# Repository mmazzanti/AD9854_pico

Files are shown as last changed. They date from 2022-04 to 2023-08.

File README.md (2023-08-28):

# PicoDDS
A Raspberry Pico PCB board that can interface with the AD9854 (and similar others) DDS chips or evaluation boards through parallel port.

# V1.0_beta (future release)
This new version addresses one of the problems in the previous board (see release 0.9), the limit on the LDO current. The new version includes a LT1086 3.3V capable of up to 1.5A. This LDO version however is slightly obsolete, I would suggest to move to a LT1963A for future. At the moment I'm very satisfied with the version 0.9 and even if the LDO is at its limits and getting quite hot the board performs well since production (~ 4 months ago) in our lab.

### Please use always the last firwmare code provided, this is independent on the board version and getting updated/fixed from time to time.
<a href="https://www.buymeacoffee.com/mmazzanti" target="_blank">Buy Me A Coffee</a>

# V0.9
## Why ?
This project was inspired by the necessity of having a simple python/serial interface to easily control older DDS evaluation boards (e.g. the  Eval-AD9854 here described).

The [Eval-AD9854](https://www.analog.com/en/design-center/evaluation-hardware-and-software/evaluation-boards-kits/EVAL-AD9854.html "Eval-AD9854") is an "old" evaluation board for the [AD9854](https://www.analog.com/en/products/ad9854.html "AD9854") Analog Devices DDS IC. The board permits programming of the AD9854 through a serial or parallel interface. 

While the AD9854 is still alive and in production at the time of writing, the word "old" refers to the serial port interface used in the Eval-AD9854 boards. 

Even though the provided software is not compatible with current Microsoft windows version the hardest part of programming the evaluation board comes from finding a parallel printer cable, perhaps from some electronics "museum".

If you are wondering what the parallel printer port on the Eval-AD9854 looks like, here it is:

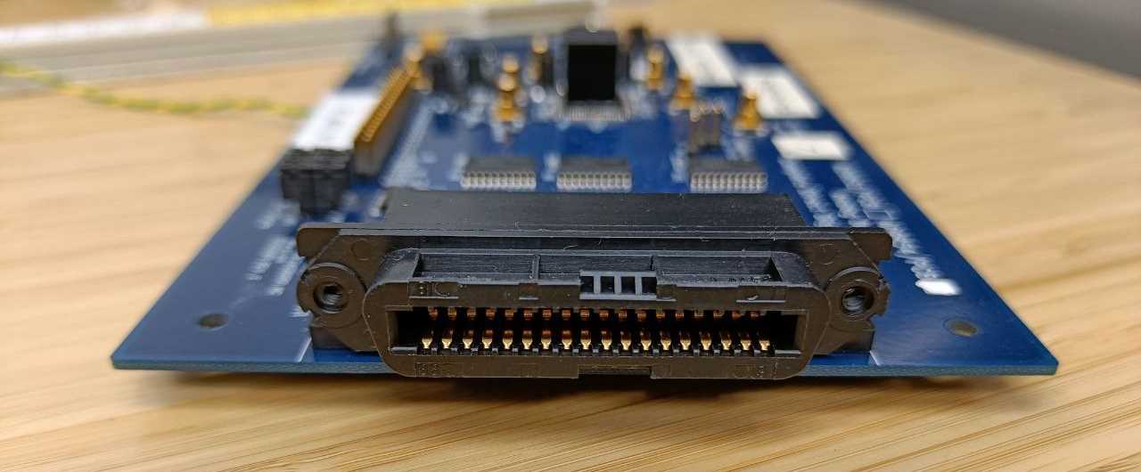
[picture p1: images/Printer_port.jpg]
Parallel_printer Parallel printer connection for millenials and older


Lukily this is not the only interface for programming the evaluation board. A 40 pins IDE port is also available on the board:

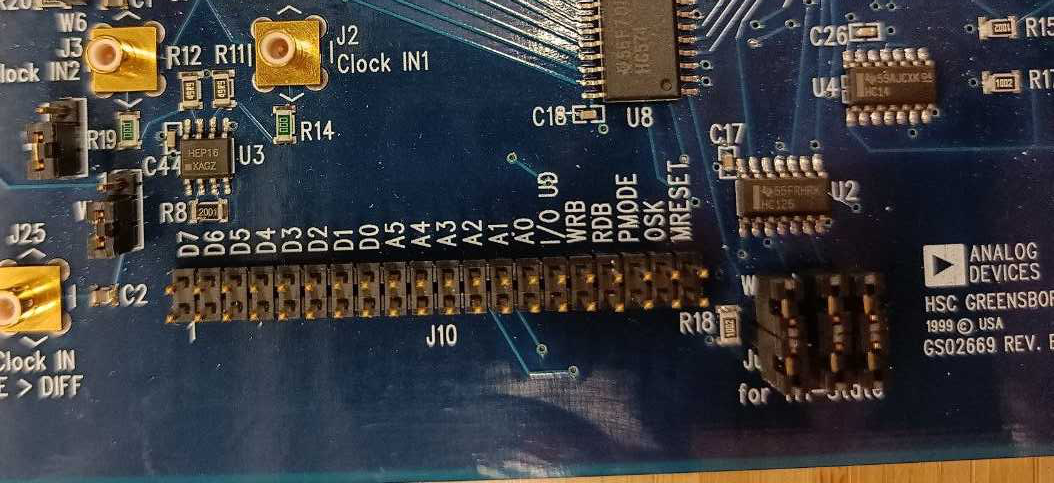
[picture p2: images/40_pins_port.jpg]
40_pins_port The 40 pins IDE port on the Eval-AD99854 board


This looks like a perfect match for any Raspberry Pi board! A custom cable from a Raspberry Pi 3/4 to the Eval-9854 board could be made (as I did for the first prototyping), but this will require a cable per each DDS and a lot of soldering. 
A better idea would be to design a PCB board that interfaces a Raspberry Pi with the DDS evaluation board.
## Why the Pico ? Can I use any Raspberry Pi ?

Sure, any microcontroller capable of handling 21 digital pins can do the job. I decided on  a Raspberry Pico just because of its price tag and small form factor.

## How about powering up the board? 

The evaluation board needs a 3.3V power source to operate. This can also be provided by the same Raspberry. **BEWARE The Eval-9854 can request up to 1A of current at 3.3V, not all Raspberry pi boards can source that amount of power**. When not using the sinc filtering function of the DDS the power consumption goes reduces to ~750mA, when prototyping I used a Raspberry pi 400 and it handled the power hungry DDS quite decently. I would however suggest to power this board externally. The PCB board in this repository takes care also of that. I added a 1A LDO with a screw terminal where one can connect power cables to the Eval-9854; not very elegant, I know,but practical. 

## How to load the "firmware" on the board ? 

Once you are in possession of a PicoDDS board you will have to load on the Raspberry Pico the python source file that you find in the /src folder. The programming of the Pico happens through its micro USB connection. **The USB connection on the board is only for powering the Pico and the Eval-9854; it cannot be used to transfer data to the board!!**

First load a UF2 micropython image on your board (guide [here](https://www.raspberrypi.com/documentation/microcontrollers/micropython.html "micropython")) then load the /src/main.py script on your board. You can do that using [Thonny](https://thonny.org/ "Thonny"), VS code or whatever IDE is now in vogue.

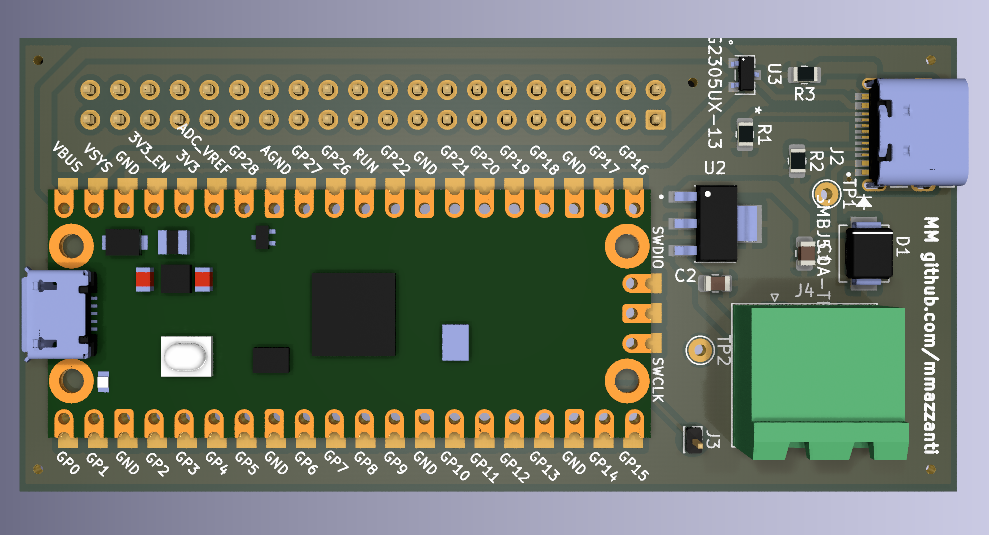
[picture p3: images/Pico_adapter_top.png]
PCB_top|400 PCB board + Raspberry Pico for AD9854


## How to program the AD9854 ? 

The AD9854 permits various modes of operation:
- Single tone mode : in this mode we output a single pre-programmed frequency
- FSK : In this mode it is possible to switch between two pre-programmed frequencies
- Ramped FSK : As the previous but with ramping the frequency up/down when switching
- Chirp : A.k.a. as pulsed FM mode, starting from an initial frequency it ramps up (linearly or not linearly) for the programmed time.
- BPSK : Select between two pre-programmed phase offsets

More precise description can be found on the AD9854 datasheet.

## Why do I need this ?

My tipycal day usage of the AD9854 is to drive some AOM in our laboratory (check out [here](http://hyqs.nl/ "Hyqs") why we want to do that).

An [AOM](https://www.rp-photonics.com/acousto_optic_modulators.html "AOM") (Acousto Optic Modulator) is nothing more than a cyrstal vibrating at a certain frequency capable of steering a laser beam and adding-subtracting its resonating frequency to the diffracting beam (read more here ).

The typical resonating frequencies of AOM are between 70-300MHz although the coverage of this bandwith is mostly wavelength dependent.

In my case I needed a signal at 150MHz and I appeared to have found some Eval-AD9854 boards in some "storage" around (what a lucky find :blush: )

## Clocking the AD9854

One of the parameters hard coded in the main.py file is the clocking speed. The AD9854 can be clocked at 300MHz max. It has an internal PLL clock multiplier in case only slower clocks are available. The board I've been using so far has a 60MHz oscillator on it, however for more phase-dependent applications I plan to use a 10MHz clock reference from an atomic clock in future. The maximum clock multiplier is 20 that would mean that using directly a 10MHz clock and a x20 multiplier will push my clocking speed to 200MHz. In this case one can use a second DDS to generate a higher frequency clock or a second PLL clock multiplier.

Set the following variables depending on your clocking speed :
- SYSCLK : Provided clock speed (frequency of whatever you connect to the clock input port). In my case SYSCLK = 60E6.
- CLKMULT : Clock multiplier value, this will define the maximum frequency that can be generated by the DDS. In my case CLKMULT = 4 --> I'm clocking the DDS at 4*60MHz = 240MHz frequency and the highest output frequency I can get is 120MHz.
- WR_D_A(0x20, 0x60) : This is defined inside the _Init_AD9854()_ function. If you want to enable sinc filtering, replace it to _WR_D_A (0x20, 0x60) **BEWARE : This raises the total power consumption to 1.1A (1A AD9854 + 100mA for the Pico), which is 100mA higher than the on-board LDO's capability**. It should be enabled only when the Pico is connected through its micro-usb connection. In this configuration the mossfet will set the micro-usb as power source for the Pico and avoid over-loading the LDO. I will provide soon a V2 of the board with an updated LDO that can output up to 1.5A.
## How to use the micropython script

Various functions are available from the source script. These don't cover all the capabilities of the AD9854 but only what I need in the lab. More functions might be added in the future if I need them. Feel free to fork this repository if you want to add more!

After connecting to the Pico the following functions are available from the serial terminal.

- SingleTone(freq,ampl) : Turns on the AD9854 at the input frequency. freq must be declared in hertz. This corresponds to the single tone mode of the DDS. The amplitude of the signal can be selected with the "ampl" parameter [0-4095].
- on(freq,ampl) : To be used after initializing the DDS (by calling _SingleTone()_). Sets the output frequency and amplitude in single tone operational mode.
- off() : Turns off the DDS output (sets it to the lowest amplitude).
- UFSK(freq1, freq2, ampl) : Sets the AD9854 in FSK mode, the lowest frequency between freq1 and freq2 will be outputted immediately. To switch between the two frequencies one can use the Switch() function.
- RUFSK(freq1, freq2, ampl, delta, N) : Switches between freq1 and freq2 going through a linear ramp between the two. This corresponds to the ramped-FSK mode of the DDS. N is the number of steps the counter will need before switching to the next frequency. The switching period is given by (N-1)*system_clock. "delta" is the frequency step incremented each time the counter reaches 0
- Switch() : Switches between freq1 and freq2.

## No, I don't want to order your board!

Then no problem, the board just simplifies the connection. If you don't want to order a board or just test if the DDS works for you or any other reasons you can just connect 20 of the 40 pins connection to your Raspberry Pico (or 3/4) and start using generating RF frequencies immediately!
<br/>
<br/>
**BEWARE :** powering the DDS is now up to you. Find a 3.3V 1A power source (better if 1.5A).
<br/>
<br/>
Connect the Pico and the Eval-9854 as following:

- GP16 -> MRESET
- GP15 -> OSK
- GP17 -> PMODE
- GP14 -> RDB
- GP18 -> WRB
- GP13 -> I/O UD
- GP2 -> FSK (this can be found on the pin W9 on the board)
- GP19 -> A0
- GP12 -> A1
- GP20 -> A2
- GP11 -> A3
- GP21 -> A4
- GP10 -> A5
- GP22 -> D0
- GP9 -> D1
- GP8 -> D2
- GP7 -> D3
- GP6 -> D4
- GP5 -> D5
- GP4 -> D6
- GP3 -> D7

Or replace the Pins number in the python source file. A Raspberry pico can be connected using dupont wires as following :

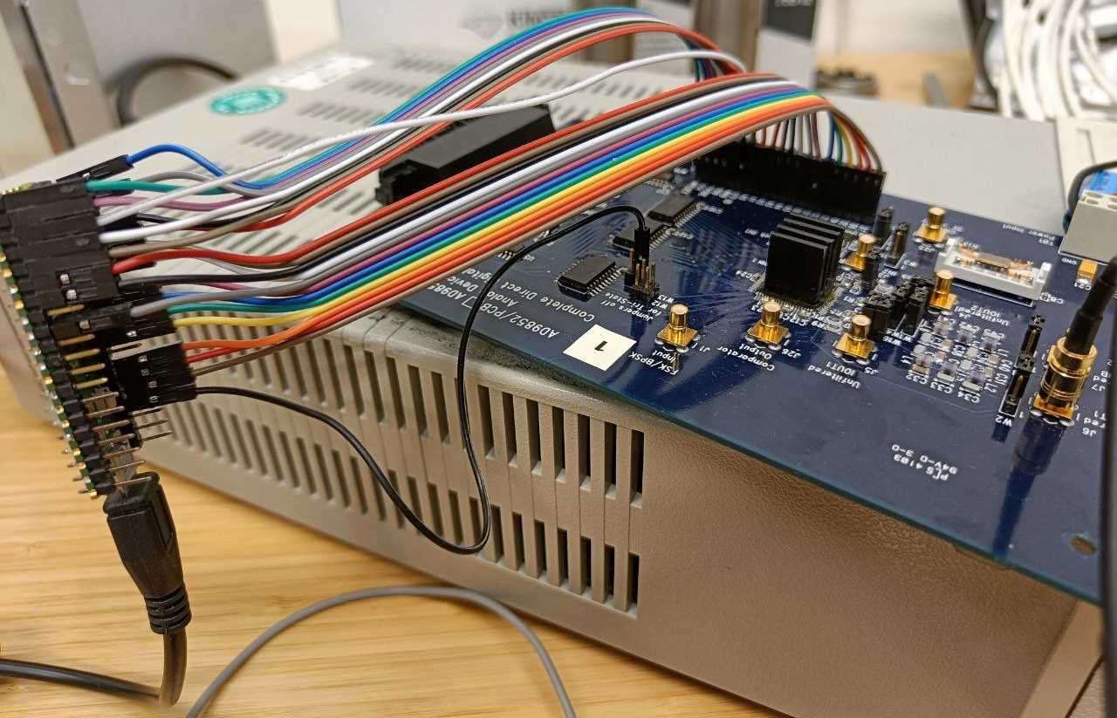
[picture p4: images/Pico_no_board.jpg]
Pico_no_board|400 A Raspberry Pico connected to an Eval-AD9854 using dupont wires


Notice the black wire going on the pin W9, this is used for the FSK bit.

## Performances

### Switching time :

Time required to switch off -> on the RF signal.
It takes ~6ms from the moment one calls the _on(freq,ampl)_ (T=0 in the picture) to the moment when the AD9854 gives an output. 
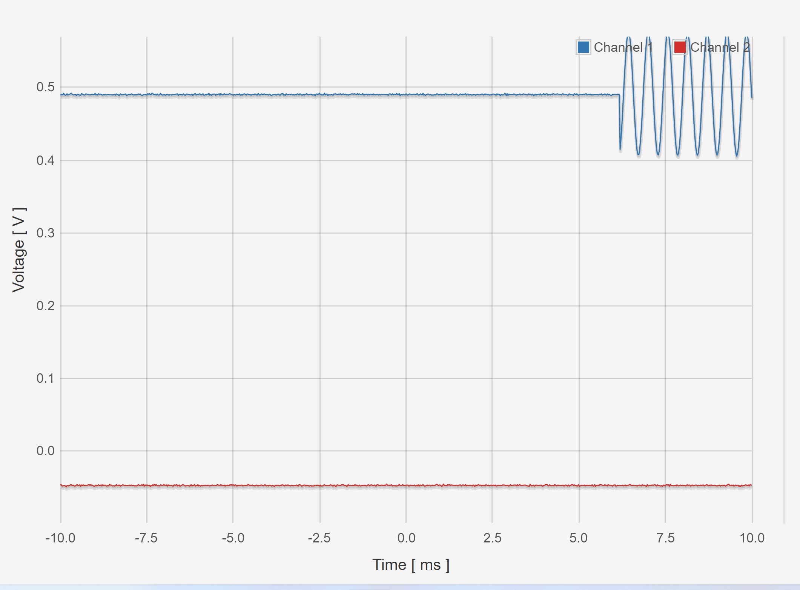
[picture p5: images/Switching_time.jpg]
Switching time On/Off switching time


### Frequency sweep :

This is an example of a frequency sweep :

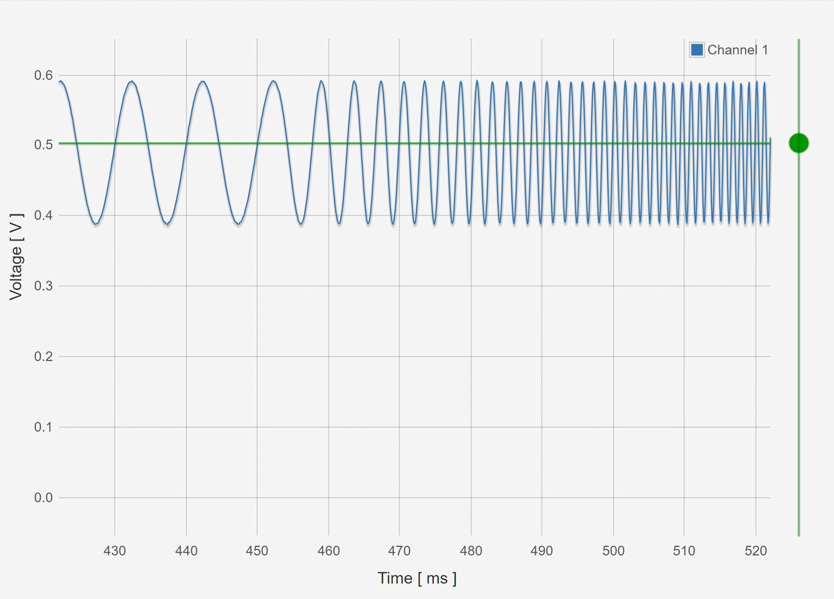
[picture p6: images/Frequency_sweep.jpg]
Frequency sweep


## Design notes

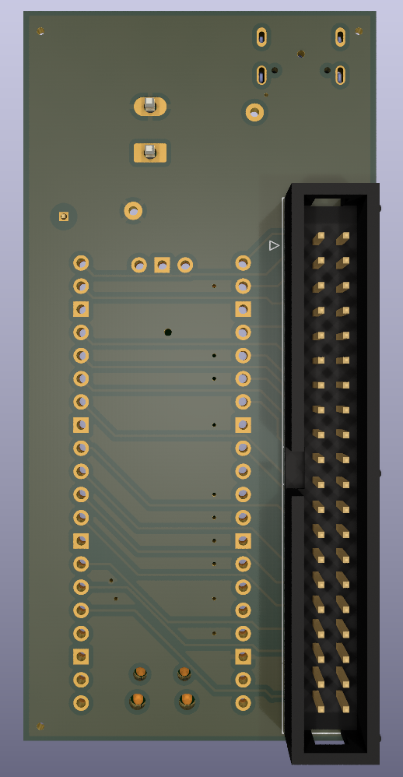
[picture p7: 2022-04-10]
images/Pico_adapter_bottom.png

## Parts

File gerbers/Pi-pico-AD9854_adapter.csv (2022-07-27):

Id | Designator | Package | Quantity | Designation | Supplier and ref
1 | U2 | LT1086 | 1 | LT1086-3.3
2 | TP2,TP1 | TestPoint_THTPad_D2.0mm_Drill1.0mm | 2 | TestPoint
3 | R1,R2 | R_0805_2012Metric | 2 | 5.1k
4 | J4 | PhoenixContact_MSTBA_2,5_2-G-5,08_1x02_P5.08mm_Horizontal | 1 | Screw_Terminal_01x02
5 | D1 | SMBJ5.0A-TR | 1 | SMBJ5.0A-TR
6 | U3 | DMG2305UX-13 | 1 | DMG2305UX-13
7 | U1 | RPi_Pico_SMD_TH | 1 | Pico
8 | R3 | R_0805_2012Metric | 1 | 0
9 | J2 | HRO_TYPE-C-31-M-12 | 1 | TYPE-C-31-M-12
10 | C2,C1 | CP_EIA-2012-12_Kemet-R | 2 | 10uF
11 | J3 | Pin_D1.0mm_L10.0mm | 1 | Conn_01x01_Male
12 | J1 | IDC-Header_2x20_P2.54mm_Vertical | 1 | Conn_02x20_Odd_Even

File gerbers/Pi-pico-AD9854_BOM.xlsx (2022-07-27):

Comment | Designator | Footprint | JLCPCB Part #
0.47 uF | C1 | CAP-SMD_0805 | C13967
33uF | C2 | CAP-SMD_0805 | C432920
SMBJ5.0A-TR | D1 | SMB,DO-214AA | C130397
TYPE-C-31-M-12 | J2 | TYPE-C-31_L8.94_W7.3 | C165948
C81276 | J3 | SIP-1_2.54x2.54 | C81276
Screw_connector_terminal | J4 | SIP-2_7.8x10.0x5.0P | C8404
5.1K | R1 | RES-SMD_0805 | C17617
5.1K | R2 | RES-SMD_0805 | C17617
0 | R3 | RES-SMD_0805 | C728267
LT1086IM-3.3#TRPBF | U2 |  | C662441
DMG2305UX-7 | U3 | SOT-23-3 | C150470

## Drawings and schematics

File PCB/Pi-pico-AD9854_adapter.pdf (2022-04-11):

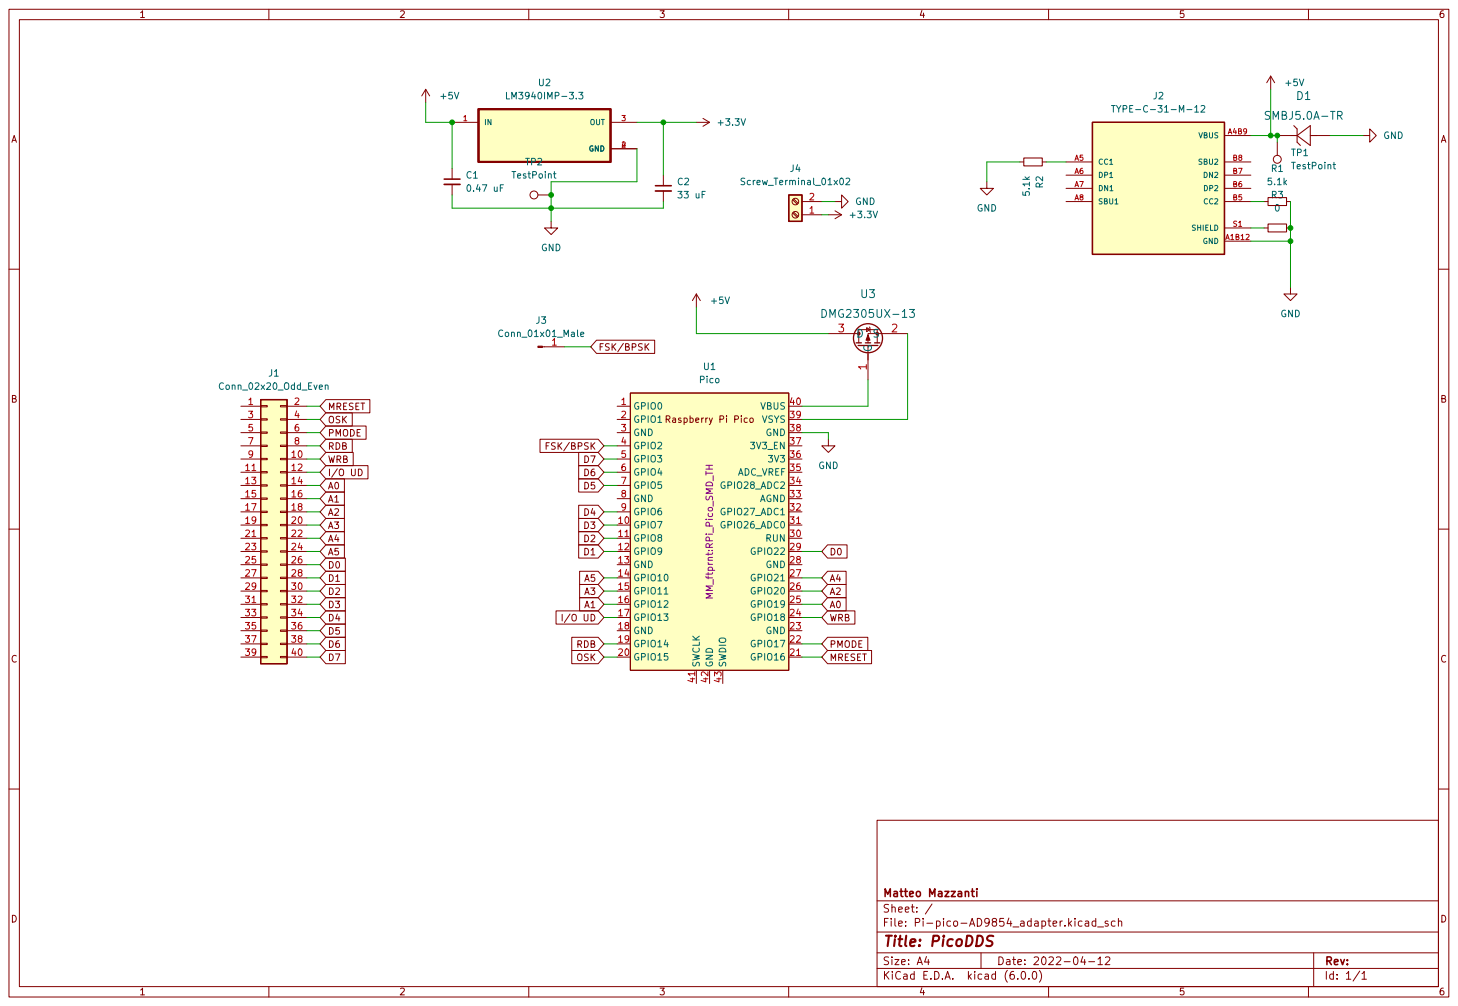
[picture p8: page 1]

File: Pi-pico-AD9854_adapter.kicad_sch Sheet: / Matteo Mazzanti

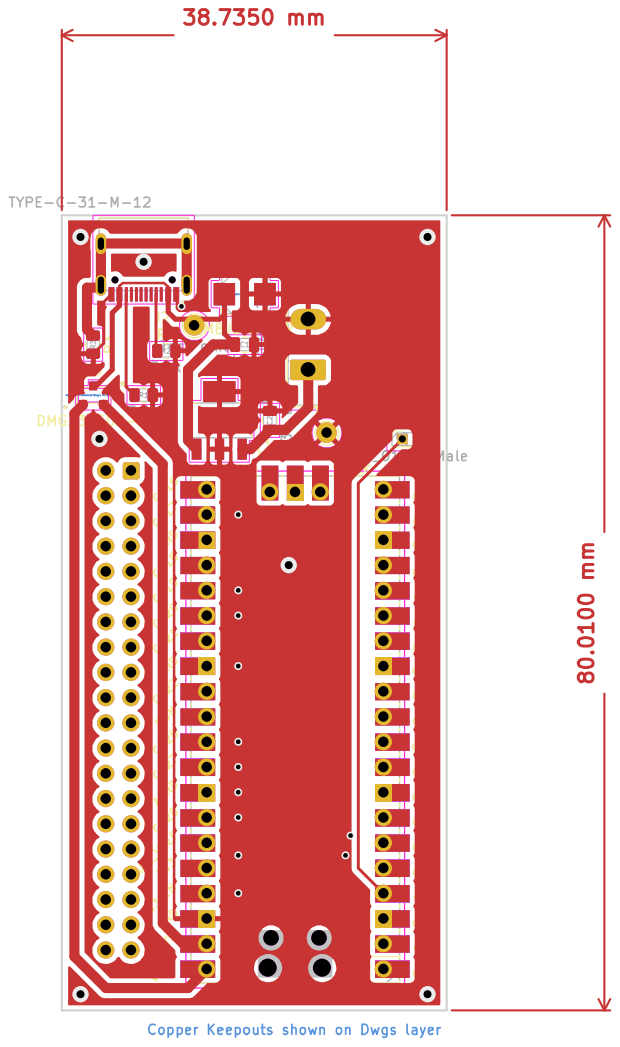
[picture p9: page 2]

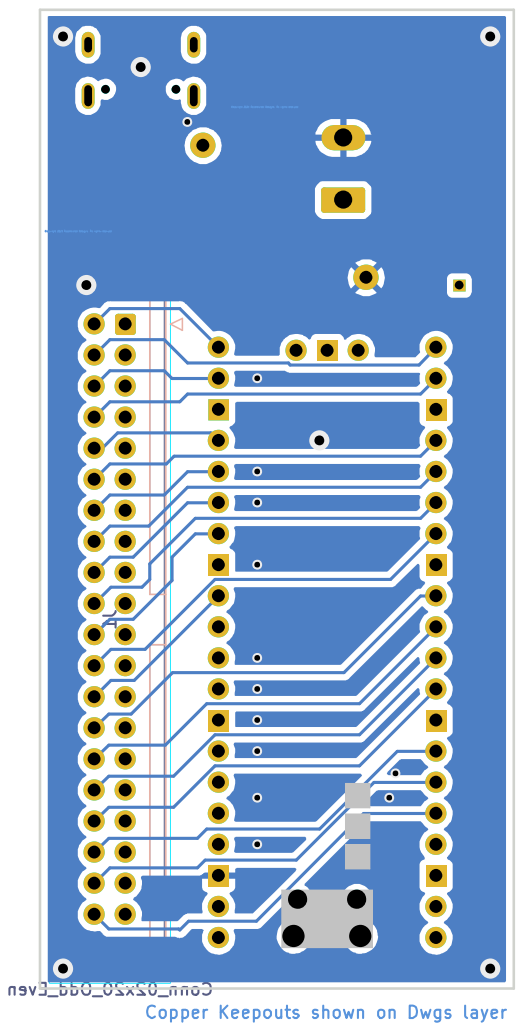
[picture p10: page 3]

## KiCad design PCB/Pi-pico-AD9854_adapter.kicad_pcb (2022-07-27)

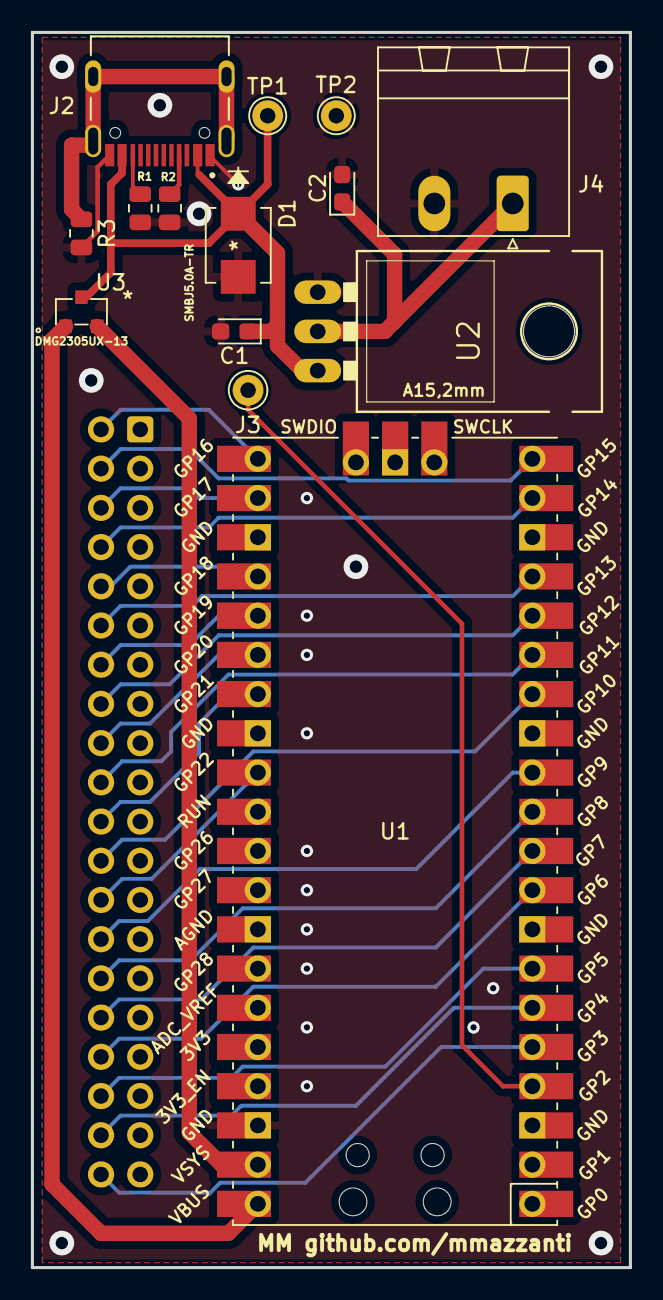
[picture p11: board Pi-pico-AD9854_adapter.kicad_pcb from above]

Board: 2 copper layers, 38.7 x 80.0 mm, 15 parts (1 on the bottom side), 29 nets.

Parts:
C1, C2: 10uF; CP_EIA-2012-12_Kemet-R
D1: SMBJ5.0A-TR
J1: Conn_02x20_Odd_Even; IDC-Header_2x20_P2.54mm_Vertical
J2: TYPE-C-31-M-12; HRO_TYPE-C-31-M-12
J3: Conn_01x01_Male; Pin_D1.0mm_L10.0mm
J4: Screw_Terminal_01x02; PhoenixContact_MSTBA_2,5_2-G-5,08_1x02_P5.08mm_Horizontal
R1, R2: 5.1k; R_0805_2012Metric
R3: 0; R_0805_2012Metric
TP1, TP2: TestPoint; TestPoint_THTPad_D2.0mm_Drill1.0mm
U1: Pico; RPi_Pico_SMD_TH
U2: LT1086-3.3; LT1086
U3: DMG2305UX-13

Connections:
+3V3: C2.1, J4.1, U2.2 (VO)
+5V: C1.1, D1.1, J2.A4B9 (VBUS), TP1.1, U2.3 (VI), U3.3 (D)
A0: J1.14, U1.25 (GPIO19)
A1: J1.16, U1.16 (GPIO12)
A2: J1.18, U1.26 (GPIO20)
A3: J1.20, U1.15 (GPIO11)
A4: J1.22, U1.27 (GPIO21)
A5: J1.24, U1.14 (GPIO10)
D0: J1.26, U1.29 (GPIO22)
D1: J1.28, U1.12 (GPIO9)
D2: J1.30, U1.11 (GPIO8)
D3: J1.32, U1.10 (GPIO7)
D4: J1.34, U1.9 (GPIO6)
D5: J1.36, U1.7 (GPIO5)
D6: J1.38, U1.6 (GPIO4)
D7: J1.40, U1.5 (GPIO3)
FSK/BPSK: J3.1, U1.4 (GPIO2)
GND: C1.2, C2.2, D1.2, J2.A1B12 (GND), J4.2, R1.2, R2.2, R3.2, TP2.1, U1.38 (GND), U2.1 (GND)
I/O UD: J1.12, U1.17 (GPIO13)
MRESET: J1.2, U1.21 (GPIO16)
unnamed: J2.A5 (CC1), R2.1
unnamed: J2.B5 (CC2), R1.1
unnamed: J2.S1 (SHIELD), R3.1
unnamed: U1.39 (VSYS), U3.2 (S)
unnamed: U1.40 (VBUS), U3.1 (G)
OSK: J1.4, U1.20 (GPIO15)
PMODE: J1.6, U1.22 (GPIO17)
RDB: J1.8, U1.19 (GPIO14)
WRB: J1.10, U1.24 (GPIO18)

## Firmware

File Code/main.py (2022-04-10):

from machine import Pin
import time


# Set here the input clock, I'm using a board with a 20MHz oscillator
# Set to 10MHz if connected to the atomic clock 
SYSCLK = 60E6;
# Set clock multiplier (that will determine the frequency precision)
# Max output freq is 1/2 F * (MULT * CLK)
# The AD9854 has an internal PLL 
CLKMULT = 4;

# Addresses for F1 & F2
addrF1 = 4;
addrF2 = 10;
addrDelta = 16;



# Define the GPIO pins
mreset = Pin(16, Pin.OUT) 
osk = Pin(15, Pin.OUT) 
pmode = Pin(17, Pin.OUT) 
rdb = Pin(14, Pin.OUT) 
wrb = Pin(18, Pin.OUT) 
ioud = Pin(13, Pin.OUT)
fsk = Pin(2, Pin.OUT)
a0 = Pin(19, Pin.OUT) 
a1 = Pin(12, Pin.OUT) 
a2 = Pin(20, Pin.OUT) 
a3 = Pin(11, Pin.OUT) 
a4 = Pin(21, Pin.OUT) 
a5 = Pin(10, Pin.OUT) 
d0 = Pin(22, Pin.OUT) 
d1 = Pin(9, Pin.OUT) 
d2 = Pin(8, Pin.OUT) 
d3 = Pin(7, Pin.OUT) 
d4 = Pin(6, Pin.OUT) 
d5 = Pin(5, Pin.OUT)
d6 = Pin(4, Pin.OUT)
d7 = Pin(3, Pin.OUT)

trigger = Pin(0, Pin.OUT)

led = Pin(25, Pin.OUT)


addresses = [a5, a4, a3, a2, a1, a0]
datas = [d7, d6, d5, d4, d3, d2, d1, d0]
masks = [int('10000000', 2), int('01000000', 2), int('00100000', 2), int('00010000', 2), int('00001000', 2), int('00000100', 2), int('00000010', 2), int('00000001', 2)]
masks2 = [int('00100000', 2), int('00010000', 2), int('00001000', 2), int('00000100', 2), int('00000010', 2), int('00000001', 2)]

def WR_D_A(addr, data):
    # Write data to address
    for i,a in enumerate(addresses) :
        a.on() if addr & masks[i+2] == masks[i+2] else a.off()
        #print("a",i,": on") if addr & masks[i] == masks[i] else print("a",i, ": off")

    # Write data to data
    for j,d in enumerate(datas) :
        d.on() if data & masks[j] == masks[j] else d.off()
        #print("d",i,": on") if data & masks[i] == masks[i] else print("d",i, ": off")
    wrb.off()
    wrb.on()
    
    #print(addr&int('11111111', 2), " : ",data&int('11111111', 2))

# Clocks the external update clock 
# this works if pin 20 is set to 0 when writing the registers
# otherwise the internal clock has to be used an synchronized to the raspberry
def Update_CLK():
    ioud.on()
    ioud.off()

def Init_AD9854(mode):
    # Set device in parallel mode
    pmode.on()
    # Set the WRB pin to high
    wrb.on()
    # Set the RDB pin to high
    rdb.on()
    # Set the I/O UD pin to low
    ioud.off()
    # Set the MRESET pin to high
    mreset.on()
    # Set the MRESET pin to low
    mreset.off()
    # No mode should be powered off
    # No power saving
    WR_D_A(0x1d, 0x00)
    WR_D_A(0x1e, CLKMULT)
    #Set sysmode to 0x00 (no internal update clock!)
    WR_D_A(0x1f, mode)
    #OSK EN, Keep sinc filter enabled
    #WR_D_A(0x20, 0x60)
    #OSK EN, disable sinc filter (300mA less current needed)
    WR_D_A(0x20, 0x20)
    Update_CLK()


# Resets accumulators :
# N = 2 Resets ACC 1 (10)
# N = 1 Resets ACC 2 (01)
# N = 3 Resets ACC 1 & 2 (11)
def Rst_ACC(N,mode):
    # Assuming this happens always after a init this is not needed
    #WR_D_A(0x1f, (0x00)+mode)
    WR_D_A(0x1f, (N<<6)+mode)
    WR_D_A(0x1f, mode)
    Update_CLK()

# Calculates the 2-complement of a int
def twos_comp(val, bits):
    if (val & (1 << (bits - 1))) != 0: # if sign bit is set e.g., 8bit: 128-255
        val = val - (1 << bits)        # compute negative value
    return val                         # return positive value as is


# Set_frequency sets frequency and amplitude
# Frequency (max CLK/2)
# Amplitude (max 4096)
def Set_freq(freq,ampl,N):
    # FTW for calculating the bit frequency
    FTW = round((freq*(2**48))/(SYSCLK*CLKMULT));
    # Set frequency addresses [4,9] to FTW
    for i in range(6):
        WR_D_A(N+i,FTW>>(40-8*i)) 
    # Set I channel ampl addresses 0x[21,22] to amlitude
    if ampl > 0 :
        WR_D_A(0x21, ampl>>8 )
        WR_D_A(0x22, ampl)
        # Set Q channel ampl addresses 0x[21,22] to amlitude
        WR_D_A(0x23, ampl>>8 )
        WR_D_A(0x24, ampl)
    #Update_CLK()
    
def Set_ramprate(N):
    WR_D_A(0x1a, N>>16)
    WR_D_A(0x1b, N>>8)
    WR_D_A(0x1c, N)
    

def SingleTone(freq):
    Init_AD9854(0x00)
    on(freq)

def on(freq):
    Set_freq(freq,1095,addrF1)
    Update_CLK()
    led.on()
    
def off():
    Set_freq(0,0,addrF1)
    led.off()
    trigger.off()
    
def UFSK(freq1,freq2):
    fsk.off()
    Init_AD9854(0x2)
    Set_freq(freq1,1095,addrF1)
    Set_freq(freq2,-1,addrF2)
    Update_CLK()
    led.on()
    
def RUFSK(freq1,freq2,delta,N):
    fsk.off()
    Init_AD9854(0x4)
    Rst_ACC(2,0x4)
    # Sets Ramped FSK with triangle ramp shape
    if freq1 < freq2:
        # Set initial freq
        Set_freq(freq1,1095,addrF1)
        # Set final freq
        Set_freq(freq2,-1,addrF2)
    else :
        # Set initial freq
        Set_freq(freq2,1095,addrF1)
        # Set final freq
        Set_freq(freq1,-1,addrF2)
    # Set frequency step
    Set_freq(twos_comp(delta, 48),-1,addrDelta)
    # Set period (N+1)*System CLK
    Set_ramprate(N)
    Update_CLK()
    led.on()
    
def Switch():
    fsk.toggle()

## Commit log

2022-04-10 PCB board V1
    [Pi-pico-AD9854_adapter.kicad_pcb, Pi-pico-AD9854_adapter.kicad_sch]
2022-04-10 Added documentation, turned sinc filter off by default
2022-04-10 Added gerbers and BOM
    [Pi-pico-AD9854_BOM.xlsx, Pi-pico-AD9854_adapter-B_Cu.gbl, Pi-pico-AD9854_adapter-B_Mask.gbs, Pi-pico-AD9854_adapter-B_Paste.gbp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]
2022-07-27 V1.0_beta prototype. Firwmare fixes
    [Pi-pico-AD9854_BOM.xlsx, Pi-pico-AD9854_adapter-B_Cu.gbl, Pi-pico-AD9854_adapter-B_Mask.gbs, Pi-pico-AD9854_adapter-B_Paste.gbp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]

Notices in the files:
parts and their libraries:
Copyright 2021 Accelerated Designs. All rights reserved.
